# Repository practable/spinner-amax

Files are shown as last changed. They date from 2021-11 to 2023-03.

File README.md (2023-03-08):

# spinner-amax

Spinner experiment with Maxxon AMAX 32 motor, upgraded for 2022 usage by Controls and Instrumentation 3, School of Engineering, University of Edinburgh. This design has now been used for over 2,500 hours in total across 12 separate instances. We have now expanded the fleet to 48 experiments, with 12 different weights (four of each).

You can cite the contents of this repo via this paper:

D.Reid, J. Burridge, D. Lowe, T. Drysdale "Open-source remote laboratory experiments for controls engineering education," _International Journal of Mechanical Engineering Education_, February 2022, [doi:10.1177/03064190221081451](https://journals.sagepub.com/doi/full/10.1177/03064190221081451)

<figure>
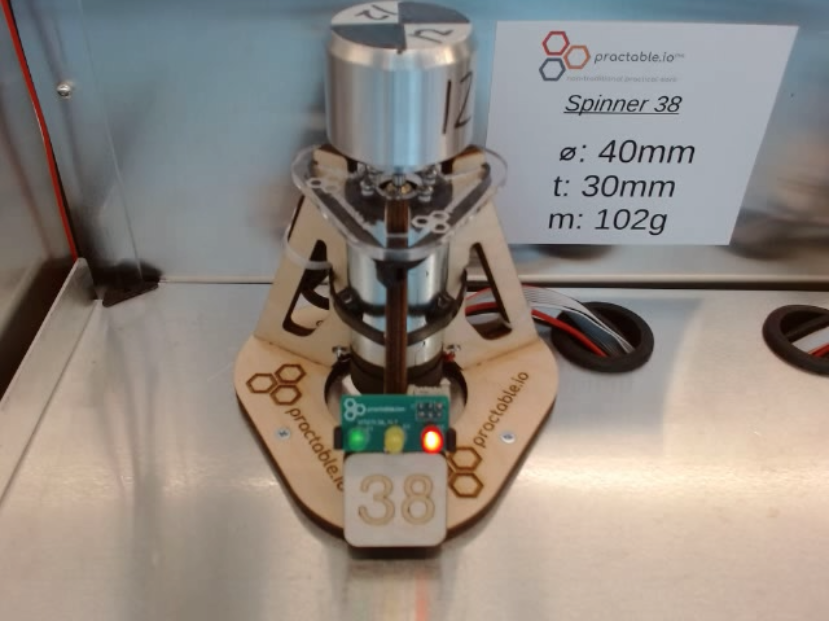
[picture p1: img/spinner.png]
Spinner hardware using Amax motor in tri-pod mount

<figcaption align = "center"><b>Fig. 1. Spinner hardware using AMAX motor</b></figcaption>
</figure>

## Contents

  - Firmware `./fw`
  - Hardware `./hw`
  - Printed Circuit Board `./hw/pcb`
  - Single Board Computer `./sbc`
  - UI `./ui`
   
## Hardware

For drawings/CAD files, please look [here](./hw/cad):

[dimensioned drawing of a weight](./hw/cad/weight-drawing.pdf)

[STEP file for the spinner experiment](./hw/cad/spinner.step)

<!--- 
<figure>
<img src="./img/spinner-cad.png"alt="3D CAD drawing of the spinner using an Amax motor in tri-pod mount" style="width:80%">
<figcaption align = "center"><b>Fig. 2. CAD drawing of the spinner hardware</b></figcaption>
</figure>
--->

### Motor

The experiment is now using an AMAX 32 motor variant (part number: 236668)

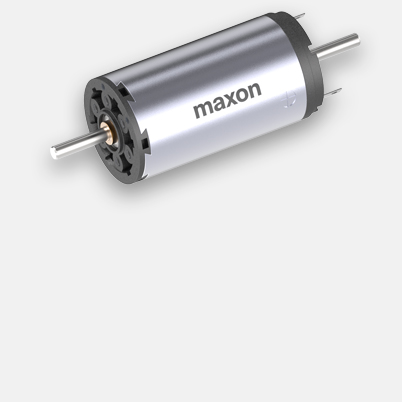
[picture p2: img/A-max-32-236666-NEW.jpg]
motor


The technical specs are [here](./hw/doc/EN-21-176.pdf/)

### Weights

The latest iteration of the weights includes attention to reducing eccentricity to reduce side load on the motor bearings.

### Previous hardware version

The first version of the hardware used a motor with siginficantly more friction, which is educationally useful although increases the challenge level for students just learning the control theory for the first time because the variability induced by the friction can obscure the presence/absence of steady state errors arising from control theory considerations. First version hardware details:  [spinner-nidec](https://github.com/practable/spinner-nidec).

## Performance

The varaibility of the step response is reduced significantly compared to the spinner using the nidec motor.
Meanwhile, here is a measured step response (average of seven runs)

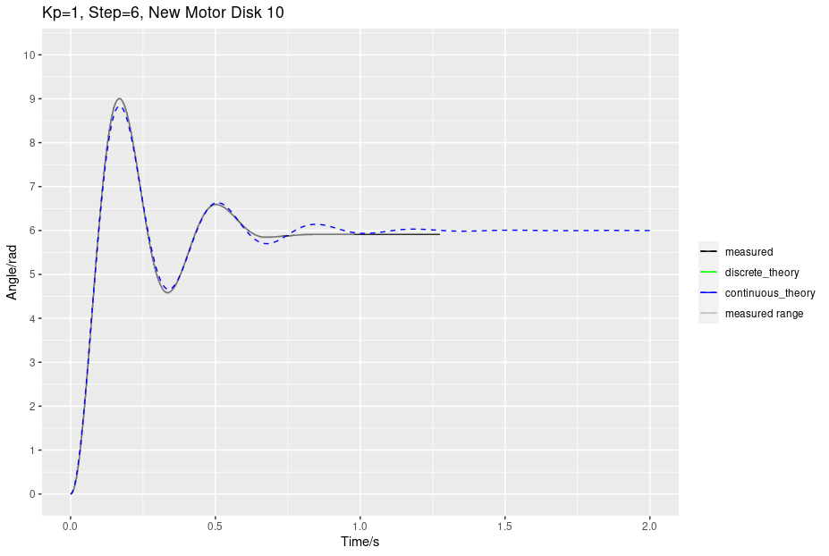
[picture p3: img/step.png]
step


## PCB

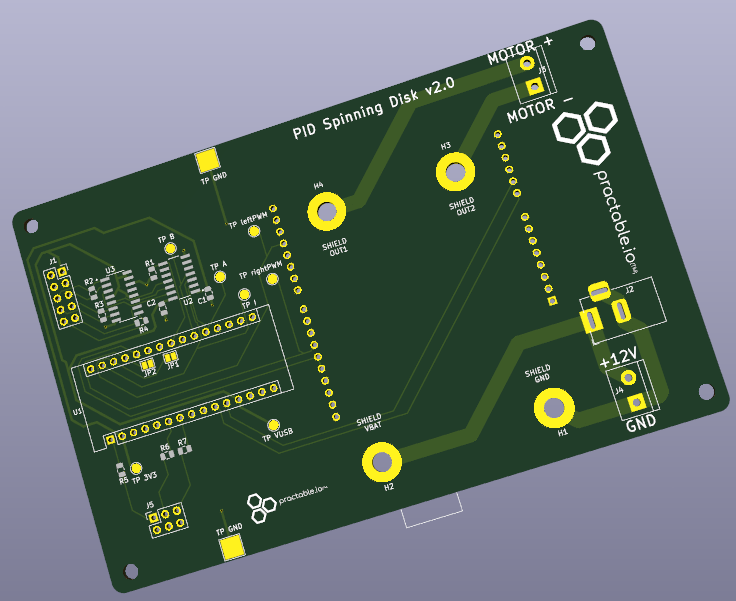
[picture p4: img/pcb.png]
pcb

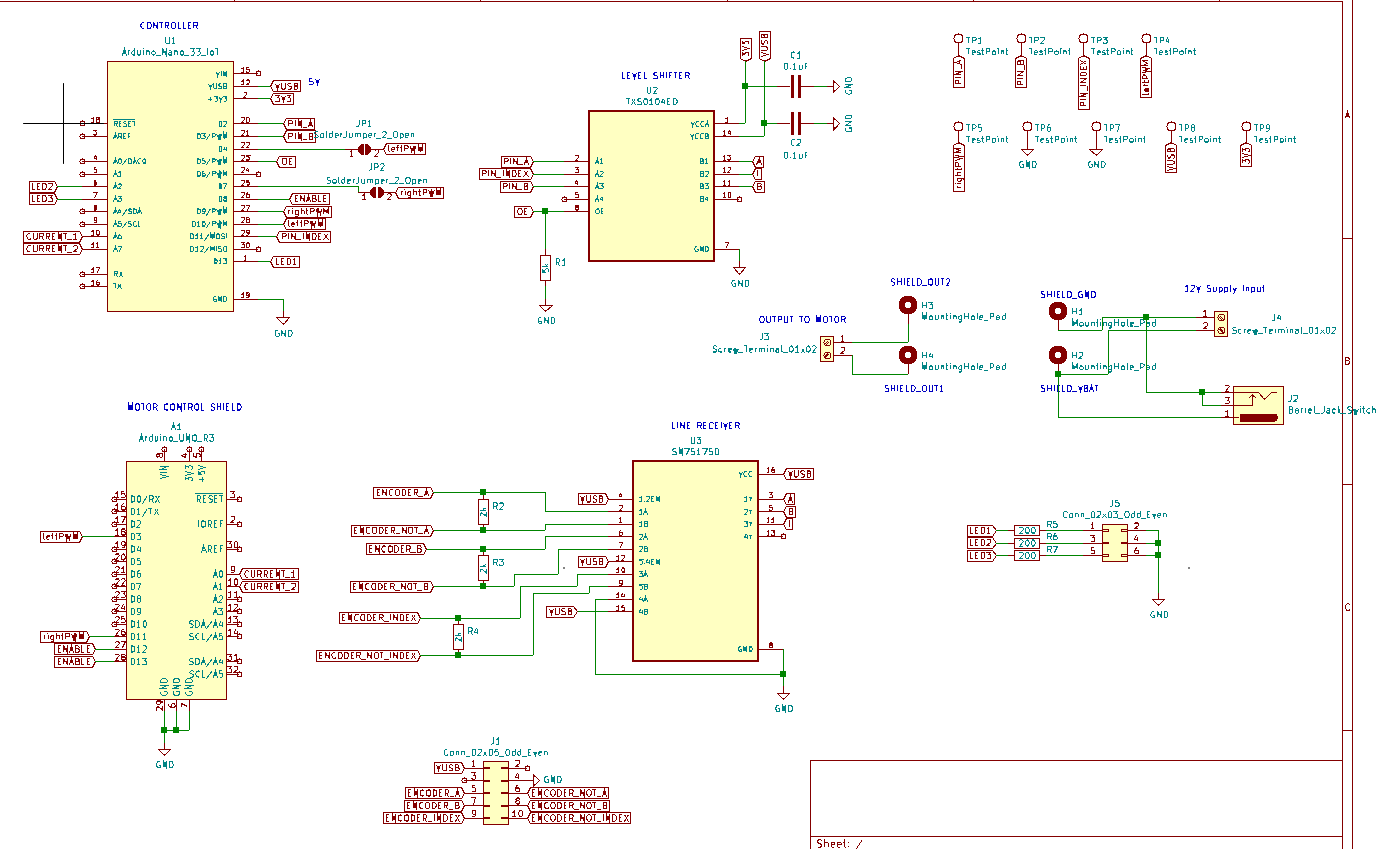
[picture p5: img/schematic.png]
schematic


## SBC

The scripts to setup your single board computer (in this case, a Raspberry Pi 4 Model B). See the [SBC README](./sbc/README.md) for instructions.

### Token refresh

Refreshing the tokens after installation is a manual process, because shell-relay currently cannot handle ansible connections.

#### Procedure

Use the configure script in `spinner-amax/sbc/scripts` to generate new tokens

```
./configure spin 30 41 https://relay-access.practable.io https://shell-access.practable.io https://shell-access2.practable.io
```

ssh into the spinners one by one (either using the shell-relay connection, or directly). If the shell tokens have expired, then a direct connection is the only option.

```
sudo su
cd /etc/practable
cat data.access #check which experiment 
rm *.token
nano data.token #copy in the token from file in ../autogenerated
nano video.token #copy in token from the file in ../autogenerated
systemctl restart session-rules
cd /usr/local/bin
mv shell shell-relay
cd /etc/systemd/system
systemctl disable shellhost #let's not use the old version any more
nano shellhost2.service #copy in file from ../autogenerated
systemctl enable shellhost2.service
systemctl start shellhost2.service
```

then check the connections to the servers

```
# in admin-tools on admin machine
./sessionrelay/getSessionStats.sh | grep spin
./shellrelay/getShellStats2.sh | grep spin
```

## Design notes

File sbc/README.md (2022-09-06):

# rpi-spinnner-2.0
How to set up a Raspberry Pi to run a spinner 2.0 experiment. 

The process is fairly simple
0. Image an SD Card with RPI OS Lite and configure it to allow ssh
0. Connect up to RPI to power, network and a Nano IoT33 
0. Log in to check you have ssh access
1. Run a configure script on your admin machine
2. Run three ansible playbooks on your admin machine (which set things up on the rpi over ssh)
3. Reboot your RPI
3. Your experiment should be working

## Abbreviations

- BYOD - Bring Your Own Device
- OS - Operating System
- SBC - single board computer (Raspberry Pi, Odroid, etc)

## Formatting

### Trimming information

`<snip>` is used to denote that line(s) have been removed for clarity

```
something useful
<snip>
other useful stuff
```

#### repo location

`$this_repo` is used to indicate the root of the git repo for clarity in the documentation, and does not actually occur in any of the scripts.

### Indicating where to enter commands?

Code snippets will sometimes clarify which machine they should be run on, if it is not obvious from the context. E.g. your local admin machine:
```
# local
$ <some commands>
```

or on the raspberry pi (via the ssh connection you've established from your local machine). 

```
# rpi
$ <some command>
```

## Prequisites

### Hardware

This is our tested configuration. 

- Raspberry Pi 4 Model B 4 GB RAM 
- SD Card 32 GB, Class 10
- USB A to micro B cable for arduino
- Arduino Nano IOT33
- USB Webcam (Logitech C920)
- USB C power cable
- RJ45 Ethernet connection (avoid WiFi because it is laggy for users)
	
For assembling the full experiment, you will also need some additional items that are outside the scope of this repo:
- Spinner PCB including Infineon motor driver board
- Spinner hardware (stand, motor, encoder, disk)
- Experimental tray and 1/6th scale shipping container

### Software

The setup is best done from a linux machine. We have no plans to support commercial operating systems.

- Linux 
   - recommend Ubuntu 20.04 LTS
- Raspberry Pi Imager
   - [github](https://github.com/raspberrypi/rpi-imager) (see link in README for latest download location)
- Practable's [relay](https://github.com/practable/relay) 
    - ensure the `sessionrelay` and `shellrelay` commands are in your path 
- Ansible 
   - Tasks developed with v2.9.17 and python 3.7.4
   - [Installation](https://docs.ansible.com/ansible/latest/installation_guide/intro_installation.html)
   
### Information

You will need either access tokens or the access secret(s) to your relay(s). Your site administrator for practable will advise. These scripts are written for the case you have the secret. If you have been provided some tokens, you just copy them into `$this_repo/autogenerated` and skip some steps where indicated.

We assume that your relay access secret is the same for all the relays in use, and available at `~/secret/practable.pat`. That way, it's not in the repo.

### Network

You need a wired staging network where unknown devices can obtain an IP address via DHCP. Your admin machine is ideally also in the same subnet as your RPI. If you are at work/university, then you will need to create your own staging network because most institutional networks prevent unknown devices from accessing the wired networks. Without a staging network, you are are stuck in a catch-22 of not knowing enough about the device to get that permission for access to the production network (typically a BYOD network for devices that staff and students might bring in).

Good staging networks: your home network (no re-configuration is needed) or a linux laptop with a wifi connection and an RJ45 dongle (share the wifi to the dongle) - I use one for initial setups and the other for ad-hoc direct connections to experiments during field-testing.

### User environment

#### Mandatory

None listed

#### Optional

If you see `ap` in the commands here, it's due to my habitual usage of a zsh alias for `ansible-playbook`. You can set up the alias by adding this line to your Zsh configuration in `~/.zshrc`:

```
alias ap="ansible-playbook"
```

I'll aim to make all code-snippets here independent of that alias.

## Setup

Overview: The process starts by loading an OS onto an SD card, modifying it to permit `ssh` access, then finishing the setup over an ssh connection. There are a mixture of steps conducted on the SBC

### SBC OS

#### Base Image

Use the Raspberry Pi Imager to image your SD Card with `Raspberry Pi OS (other) ... Raspberry Pi OS Lite (32-bit)` 

Do not bother with the full version - the desktop features are not needed but use additional power.

You'll be asked to enter your sudo password and confirm the correct SD card location - best to remove other SD cards to avoid making a mistake and choosing your camera's SD card by accident.

After verifying the card is complete, it will be mounted on your system. Do not remove it from your reader yet, and leave it mounted for the next step.

#### Modifications

You should enable `ssh` - whilst the SD Card is still mounted on your computer, look for the book partition of the SD card in your file explorer.

Open the boot partition in a terminal, and create the file `ssh`

```
touch ssh
```

Exit the terminal, unmount/eject the `boot` and `rootfs` partitions, and remove the SD card from the reader.

### RPI OS

#### Find the IP address of your RPI

Before booting your RPI, you need to figure out the IP addresses of other devices on your network. In the next step, we will be looking for the IP address of the RPI, and it is easier if you already know which devices are NOT the RPI.

First, let's figure out the IP address of the wired ethernet port on your admin machine 
```
$ ip addr 
<snip>
3: enp0s31f6: <BROADCAST,MULTICAST,UP,LOWER_UP> mtu 1500 qdisc fq_codel state UP group default qlen 1000
    link/ether xx:xx:xx:xx:xx:xx brd ff:ff:ff:ff:ff:ff
    inet 192.168.0.46/24 brd 192.168.0.255 scope global dynamic noprefixroute enp0s31f6
       valid_lft 784687sec preferred_lft 784687sec
    inet6 xxxx::xxxx:xxxx:xxxx:xxxx/64 scope link noprefixroute 
       valid_lft forever preferred_lft forever
<snip>
```
Our network card is at 192.168.0.46. The first three number groups matter here. Find all the devices on the same sub-net, using that IP address by set the last number group to `1/24` which is [shorthand](https://www.ietf.org/rfc/rfc1878.txt) for 0-254 (all possible IP in the subnet).
```
$ sudo nmap -sP 192.168.0.1/24
sudo nmap -sP 192.168.0.1/24
Starting Nmap 7.80 ( https://nmap.org ) at 2022-08-25 13:18 BST
Nmap scan report for _gateway (192.168.0.1)
Host is up (0.0016s latency).
MAC Address: xx:xx:xx:xx:xx:xx 
Nmap scan report for 192.168.0.29
Host is up (0.00059s latency).
MAC Address: xx:xx:xx:xx:xx:xx 
Nmap scan report for 192.168.0.52
Host is up (0.036s latency).
MAC Address: xx:xx:xx:xx:xx:xx 
Nmap scan report for 192.168.0.62
Host is up.
Nmap done: 256 IP addresses (3 hosts up) 
```

Put the SD card in your Raspberry Pi, connect the network cable, and power on. Wait about a minute (or repeat until a new device shows up)

```
$ sudo nmap -sP 192.168.0.1/24
sudo nmap -sP 192.168.0.1/24
Starting Nmap 7.80 ( https://nmap.org ) at 2022-08-25 13:18 BST
Nmap scan report for _gateway (192.168.0.1)
Host is up (0.0016s latency).
MAC Address: xx:xx:xx:xx:xx:xx 
Nmap scan report for 192.168.0.29
Host is up (0.00059s latency).
MAC Address: xx:xx:xx:xx:xx:xx 
Nmap scan report for 192.168.0.52
Host is up (0.036s latency).
MAC Address: xx:xx:xx:xx:xx:xx 
Nmap scan report for 192.168.0.62
Host is up.
MAC Address: yy:yy:yy:yy:yy:yy (Raspberry Pi Trading)
Nmap scan report for 192.168.0.184
Host is up (0.00027s latency).
Nmap done: 256 IP addresses (4 hosts up) 
```
Now you should see a new device that is labelled as a Raspberry Pi. If this step does not work, then the SD Card is corrupt, the network cable/power are disconnected, or the router on your network is not permitting DHCP requests from unknown devices.

In this case the IP address is 192.168.0.184.

Make a note of the MAC address of your SBC so that you can share that with your network administrators at the University - sometimes you must declare the MAC address to be able to access a wired BYOD network.

#### ssh into your RPI

The standard user and password on the image is usually `pi/raspberry`

On your machine, open a terminal
```
$ ssh pi@192.168.0.184 #change to whatever IP you found in previous step

The authenticity of host '192.168.0.184 (192.168.0.184)' can't be established.
ECDSA key fingerprint is SHA256:/0jZ9w8zL4h94rojSnSQ0Yewv5G8qK2AjCod/09pBkE.
Are you sure you want to continue connecting (yes/no/[fingerprint])? yes
Warning: Permanently added '192.168.0.184' (ECDSA) to the list of known hosts.
pi@192.168.0.184's password: <--- enter the password here (usually, raspberry)

```
Then you should see something like this:

```
Linux raspberrypi 5.10.17-v7l+ #1414 SMP Fri Apr 30 13:20:47 BST 2021 armv7l

The programs included with the Debian GNU/Linux system are free software;
the exact distribution terms for each program are described in the
individual files in /usr/share/doc/*/copyright.

Debian GNU/Linux comes with ABSOLUTELY NO WARRANTY, to the extent
permitted by applicable law.

SSH is enabled and the default password for the 'pi' user has not been changed.
This is a security risk - please login as the 'pi' user and type 'passwd' to set a new password.

Wi-Fi is currently blocked by rfkill.
Use raspi-config to set the country before use.

pi@raspberrypi:~ $ 
```

Change the password 

```
$ passwd
```

Ideally we would also set up ssh certificates but this is a future step.

You can now exit the session - we will do the next steps using ansible.

```
# rpi
$ exit
```

### SBC software and configuration

We need to generate some configuration files that are customised to your experiment. Your local admin for the practable system will advise on any naming conventions that apply at your site, as well as providing the relay key(s) which you need. 

This example is written for the case of configuring a single experiment (`spin32`) which genuinely, in this case, suffered a corrupted SD card after a successful semester of usage, and needs replacing with a fresh one).

#### Ansible hosts file

We need to let ansible know about this host.

```
sudo nano /etc/ansible/hosts
```
Add in a section like this (or modify an existing section if you have one)

```
<snip>
[rpispinnerv2]
spin32 ansible_host=192.168.0.184 practable_label=spin32

[rpispinnerv2:vars]
ansible_connection=ssh
ansible_user=pi
ansible_password=***REMOVED***
<snip>
```

#### Practable connections

We need to configure routing and tokens for the video, data, shell, and shell2 connections. There are scripts provided to help you. They put files into `$this_repo./autogenerated`

Create the configuration files we need, assuming we are using the standard practable relay URLs.

```
#local
cd scripts
.configure spin 32 32 https://relay-access.practable.io https://shell-access.practable.io https://shell-access2.practable.io
```

##### Session

Now we can run our ansible playbooks - these each take some time, so get the kettle ready. It's nearly as fast doing multiple machines, because the playbooks are run in parallel. There is no need to do each RPI separately one after another.

```
#local
cd playbooks
ansible-playbook install-session
ansible-playbook install-shell
ansible-playbook install-firmware
```

If those commands go smoothly, then you are done with the install. If not, check out the troubleshooting guide below.

## Checking the installation

Go to the booking page link the adminstrator gave you, and you should be able to access/control the experiment. 

## Troubleshooting

If things are not working right, then you might be able to fix them by troubleshooting. 

### No DHCP

This is usually caused by 
- SD Card corrupt
- network administrator is unaware of the MAC address of the wired network port on the SBC

### No SSH connection

Since `sshd` is not enabled by default, you must enable it (see instructions) before incoming connections on port 22 will be accepted.

### Remote host identification has changed

If you work with a lot of experiments, sooner or later an old IP address on your staging network will be re-assigned to a new experiment you are setting up, and then you will see something like this:

```
@@@@@@@@@@@@@@@@@@@@@@@@@@@@@@@@@@@@@@@@@@@@@@@@@@@@@@@@@@@
@    WARNING: REMOTE HOST IDENTIFICATION HAS CHANGED!     @
@@@@@@@@@@@@@@@@@@@@@@@@@@@@@@@@@@@@@@@@@@@@@@@@@@@@@@@@@@@
IT IS POSSIBLE THAT SOMEONE IS DOING SOMETHING NASTY!
Someone could be eavesdropping on you right now (man-in-the-middle attack)!
It is also possible that a host key has just been changed.
The fingerprint for the ECDSA key sent by the remote host is
SHA256:/0jZ9w8zL4h94rojSnSQ0Yewv5G8qK2AjCod/09pBkE.
Please contact your system administrator.
Add correct host key in /home/tim/.ssh/known_hosts to get rid of this message.
Offending ECDSA key in /home/tim/.ssh/known_hosts:178
  remove with:
  ssh-keygen -f "/home/tim/.ssh/known_hosts" -R "192.168.0.184"
ECDSA host key for 192.168.0.184 has changed and you have requested strict checking.
Host key verification failed.
```

Simply run the suggested command, and then carry on where you left off with trying to connect over `ssh`. The command is unique each time it happens (you're overwriting an entry in the known-hosts file so it must correspond to the host causing the problem _this_ time). E.g.

```
$ssh-keygen -f "/home/tim/.ssh/known_hosts" -R "192.168.0.184"

# Host 192.168.0.184 found: line 178
/home/tim/.ssh/known_hosts updated.
Original contents retained as /home/tim/.ssh/known_hosts.old
```

### Check the OS
If you're not sure if you have the right OS for the ansible scripts, you can check. For this experiment, you should see something like this

```
$ uname -a
Linux raspberrypi 5.10.17-v7l+ #1414 SMP Fri Apr 30 13:20:47 BST 2021 armv7l GNU/Linux
```

### Ansible cannot reach rpi

If you are having trouble connecting via ansible, following the guidance on verbose logging [here](https://docs.ansible.com/ansible/latest/network/user_guide/network_debug_troubleshooting.html)

You might find you've got the format of the /etc/ansible/hosts incorrect (e.g. didn't name the vars section correctly, got the password wrong etc).

### ttyACM0 Device not found 

If you get this error, reboot the raspberry pi and try again. If the error persists, check which device name it has been assigned (`/dev/ttyACM0` is expected for Nano 33 IOT)
```
#rpi
lsusb
dmesg | tail
```

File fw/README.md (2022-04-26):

# spinner-amax-firmware
Arduino Nano 33 IOT Firmware for the [amax-spinner](https://github.com/practable/spinner-amax) hardware

## About

This firmware is intended to work with the [amax-spinner](https://github.com/practable/spinner-amax) hardware as shown in Fig. 1.

<figure>
Spinner hardware using Amax motor in tri-pod mount
<figcaption align = "center"><b>Fig. 2. Spinner hardware using AMAX motor</b></figcaption>
</figure>

The firmware is configured to use a printed circuit board designed according to the schematic in Fig. 2.
<figure>
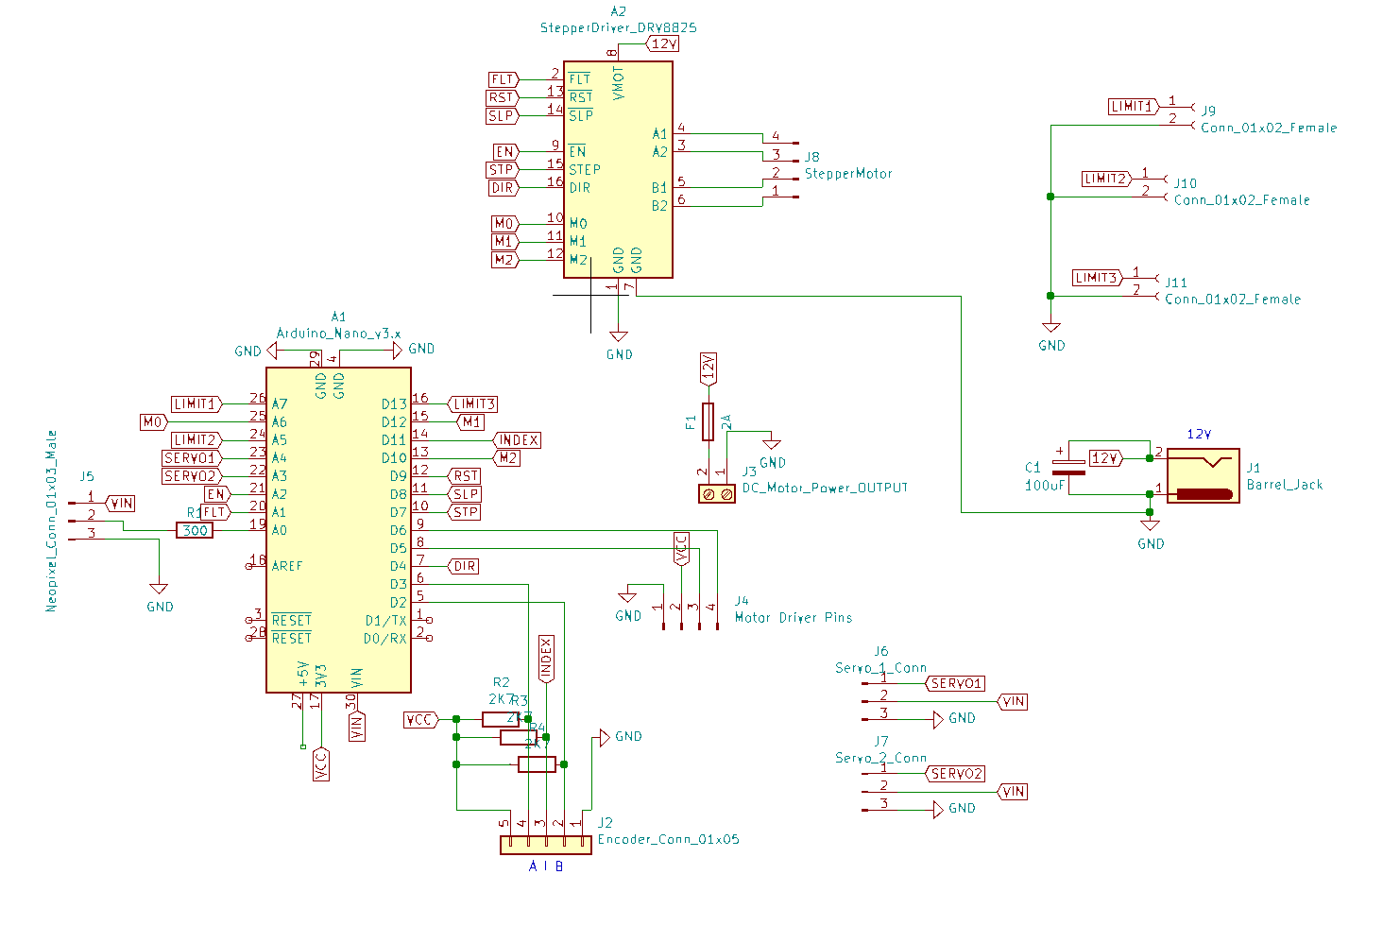
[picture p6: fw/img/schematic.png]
Spinner circuit schematic

<figcaption align = "center"><b>Fig. 2. Spinner circuit schematic</b></figcaption>
</figure>

## History

This firmware was developed in [dpreid/pidcontroller](https://github.com/dpreid/pidcontroller), and covered several different experiments based around a brushed DC motor. One of the experiments (this one) has been significantly upgraded (new motor, encoder) so the firmware has been split off into this repo to avoid confusion. The starting point for this repo is the code that was used to deliver over 2,500 hours of experiments in the early part of 2022.

## Contents

The repo contains several directories, with the code in `SpinningDiskController.`

### ./SpinningDiskController

This is the arduino firmware itself - note that the Arduino convention is to use camel case with an initial capital letter, and that the folder name should match the sketch name.

### ./libraries

These are the libraries required by the firmware 

### ./test

This directory contains tests - see [./test/README.md](./test/README.md) for details.

### ./scripts

This directory contains scripts to compile and upload, and an example ansible task for a raspberry pi running pios.

## Usage

The 'upload.sh' script will compile and upload the firmware, assuming you have a working command-line development environment for the Arduino Nano 33 IOT.

### Installing firmware on raspberry pi via cli

If you have installed the `arduino-cli` but not yet compiled for the Nano IOT 33, then add support for this hardware by 

```
arduino-cli core update-index
arduino-cli core install arduino:samd
```

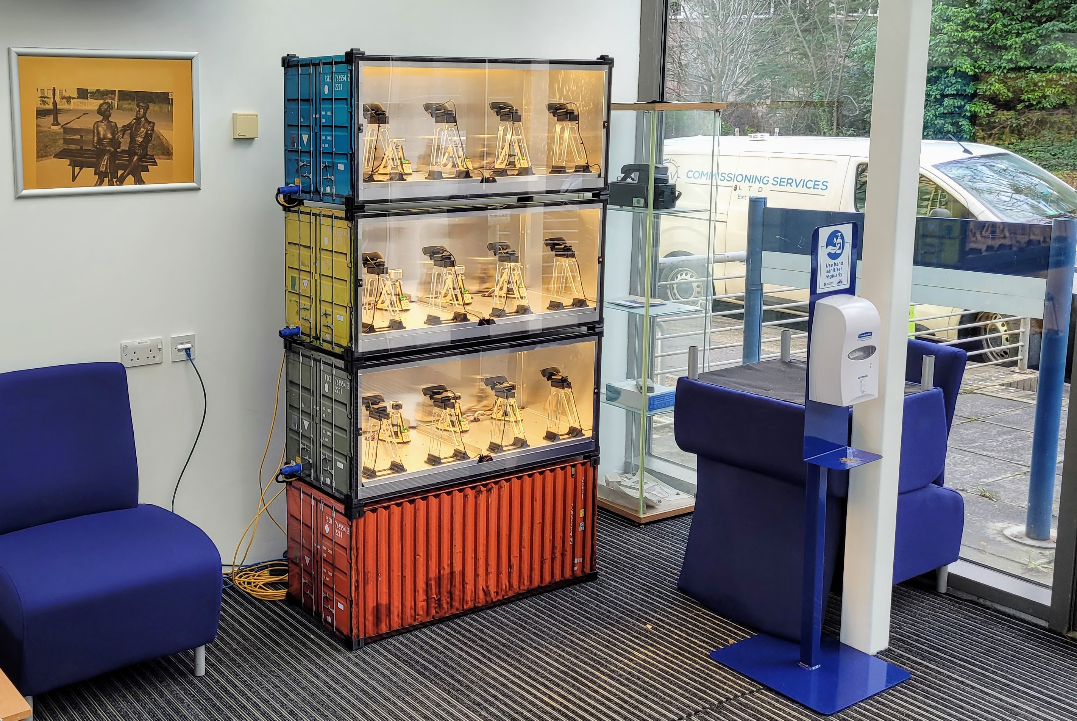
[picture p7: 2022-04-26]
fw/img/AGB_Spinners.jpg

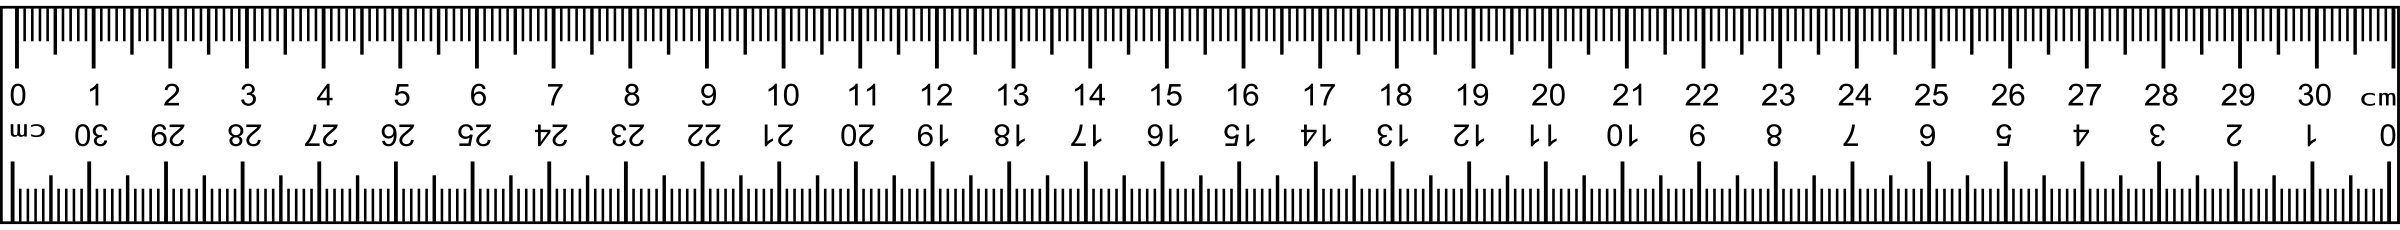
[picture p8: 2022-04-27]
ui/default/src/assets/ruler.png

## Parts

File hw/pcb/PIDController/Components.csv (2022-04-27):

Comment | Designator | Footprint | JLCPCB Part #（optional）
2k | R4,R2,R3 | R_0805_2012Metric | C17604
 | REF**,REF**,REF**,REF** | MountingHole_3.2mm_M3
 | A1 | Arduino_UNO_R3
SN75175D | U3 | SOIC127P600X175-16N
C474952 | J3,J4,J5,J6 | TerminalBlock_bornier-2_P5.08mm | C474952
 | U1 | MODULE_ABX00027
TXS0104ED | U2 | SOIC127P600X175-14N
C5665 | J1 | PinSocket_2x05_P2.54mm_Vertical | C5665
C11214 | J7 | PinSocket_2x03_P2.54mm_Vertical | C11214
 | JP1,JP2 | SolderJumper-2_P1.3mm_Open_Pad1.0x1.5mm
 | TP A,TP B,TP I,TP leftPWM,TP rightPWM,TP VUSB,TP 3V3 | TestPoint_Pad_D2.0mm
 | TP GND,TP GND | TestPoint_Pad_4.0x4.0mm
0.1uF | C1,C2 | C_0805_2012Metric | C49678
5k | R1 | R_0805_2012Metric | C78980
200 | R5,R6,R7 | R_0805_2012Metric | C17540

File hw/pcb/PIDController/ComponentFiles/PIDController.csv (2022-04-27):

Comment | Designator | Footprint | JLCPCB Part #（optional）
 | G*** | practableLogo36x15
 | G*** | practable-logo-larger
 | REF**,REF**,REF**,REF** | MountingHole_3.2mm_M3
2k | R4,R2,R3 | R_0805_2012Metric | C17604
 | A1 | Arduino_UNO_R3
SN75175D | U3 | SOIC127P600X175-16N
C474952 | J3,J4 | TerminalBlock_bornier-2_P5.08mm | C474952
TXS0104ED | U2 | SOIC127P600X175-14N
 | J1 | PinSocket_2x05_P2.54mm_Vertical
 | JP1,JP2 | SolderJumper-2_P1.3mm_Open_Pad1.0x1.5mm
 | TP A,TP B,TP I,TP leftPWM,TP rightPWM,TP VUSB,TP 3V3 | TestPoint_Pad_D2.0mm
 | TP GND,TP GND | TestPoint_Pad_4.0x4.0mm
0.1uF | C1,C2 | C_0805_2012Metric | C49678
5k | R1 | R_0805_2012Metric | C78980
200 | R5,R6,R7 | R_0805_2012Metric | C17540
 | U1 | Arduino_Nano
 | H1,H2,H3,H4 | MountingHole_4mm_Pad
 | J5 | PinSocket_2x03_P2.54mm_Vertical
 | J2 | BarrelJack_Horizontal_DC10B

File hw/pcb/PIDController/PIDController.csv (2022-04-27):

Id | Designator | Package | Quantity | Designation | Supplier and ref
1 | G*** | practableLogo36x15 | 1 | LOGO
2 | G*** | practable-logo-larger | 1 | LOGO
3 | REF**,REF**,REF**,REF** | MountingHole_3.2mm_M3 | 4 | MountingHole_3.2mm_M3
4 | R4,R2,R3 | R_0805_2012Metric | 3 | 2k
5 | A1 | Arduino_UNO_R3 | 1 | Arduino_UNO_R3
6 | U3 | SOIC127P600X175-16N | 1 | SN75175D
7 | J3,J4 | TerminalBlock_bornier-2_P5.08mm | 2 | Screw_Terminal_01x02
8 | U2 | SOIC127P600X175-14N | 1 | TXS0104ED
9 | J1 | PinSocket_2x05_P2.54mm_Vertical | 1 | Conn_02x05_Odd_Even
10 | JP1,JP2 | SolderJumper-2_P1.3mm_Open_Pad1.0x1.5mm | 2 | SolderJumper_2_Open
11 | TP A,TP B,TP I,TP leftPWM,TP rightPWM,TP VUSB,TP 3V3 | TestPoint_Pad_D2.0mm | 7 | TestPoint
12 | TP GND,TP GND | TestPoint_Pad_4.0x4.0mm | 2 | TestPoint
13 | C1,C2 | C_0805_2012Metric | 2 | 0.1uF
14 | R1 | R_0805_2012Metric | 1 | 5k
15 | R5,R6,R7 | R_0805_2012Metric | 3 | 200
16 | U1 | Arduino_Nano | 1 | Arduino_Nano_33_IoT
17 | H1,H2,H3,H4 | MountingHole_4mm_Pad | 4 | MountingHole_Pad
18 | J5 | PinSocket_2x03_P2.54mm_Vertical | 1 | Conn_02x03_Odd_Even
19 | J2 | BarrelJack_Horizontal_DC10B | 1 | Barrel_Jack_Switch

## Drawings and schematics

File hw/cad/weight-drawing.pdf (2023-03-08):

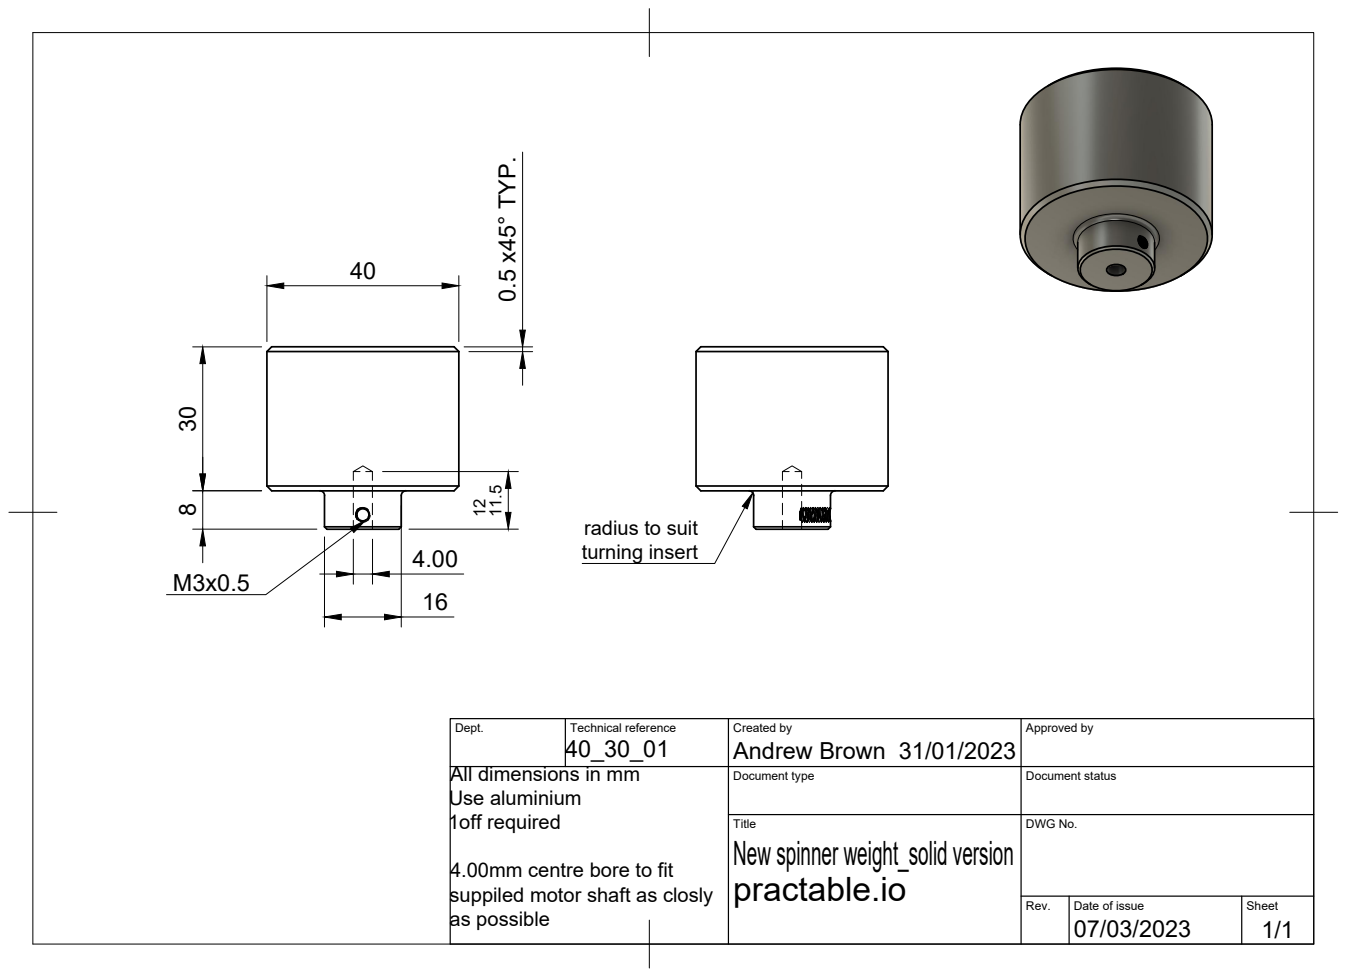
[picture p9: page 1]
as possible 30; 8 0.5 x45° TYP.

radius to suit
turning insert

Dept. | Technical reference 40_30_01 | Created by Andrew Brown 31/01/2023 | Approved by

All dimensions in mm Use aluminium 1off required 4.00mm centre bore to fit suppiled motor shaft as closly | | Document type | Document status

Title New spinner weight_solid version practable.io | DWG No.

Rev. | Date of issue 07/03/2023 | Sheet 1/1

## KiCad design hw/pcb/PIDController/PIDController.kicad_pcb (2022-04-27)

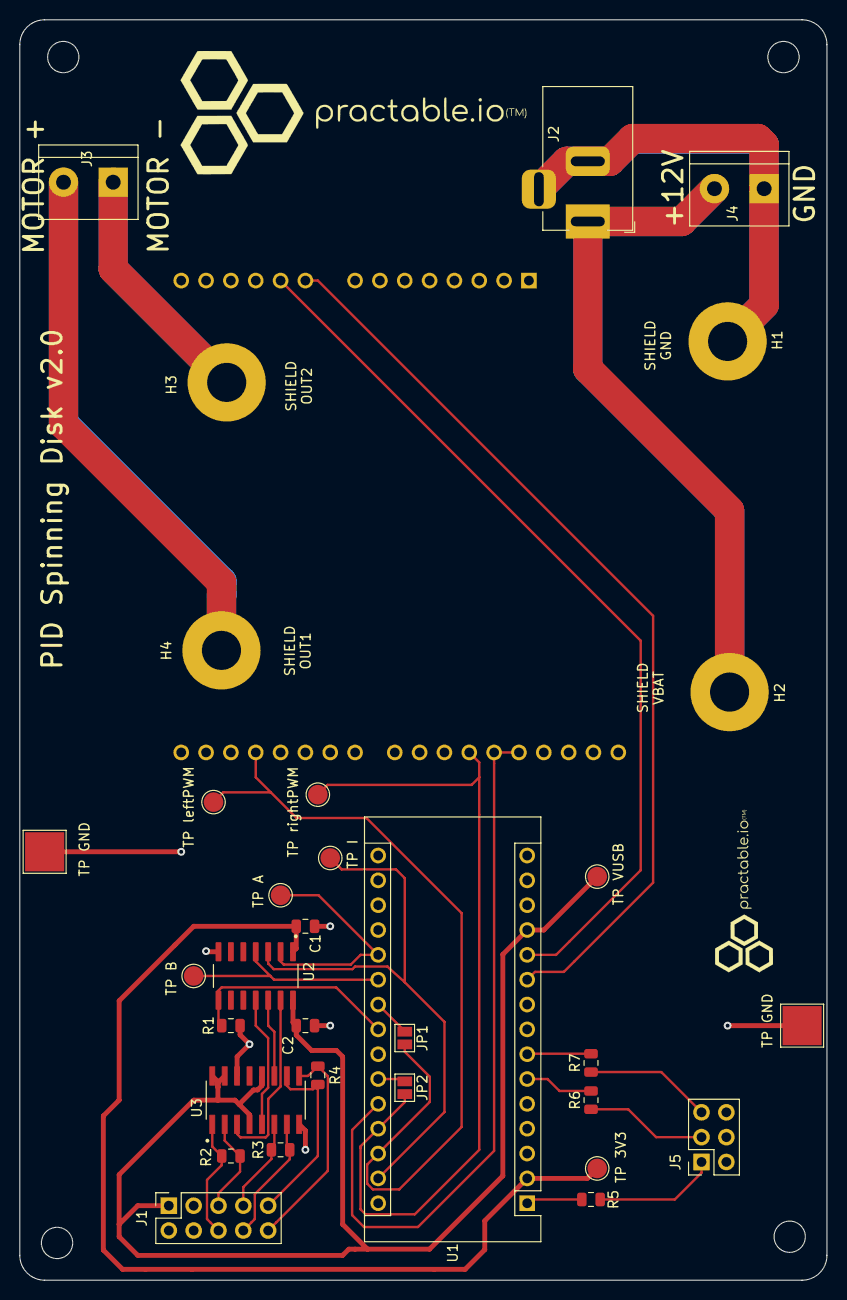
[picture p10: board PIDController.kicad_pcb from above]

Board: 2 copper layers, 82.6 x 128.9 mm, 33 parts (1 on the bottom side), 34 nets.

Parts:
A1: Arduino_UNO_R3
C1, C2: 0.1uF; C_0805_2012Metric
H1, H2, H3, H4: MountingHole_Pad; MountingHole_4mm_Pad
J1: Conn_02x05_Odd_Even; PinSocket_2x05_P2.54mm_Vertical
J2: Barrel_Jack_Switch; BarrelJack_Horizontal_DC10B
J3, J4: Screw_Terminal_01x02; TerminalBlock_bornier-2_P5.08mm
J5: Conn_02x03_Odd_Even; PinSocket_2x03_P2.54mm_Vertical
JP1, JP2: SolderJumper_2_Open; SolderJumper-2_P1.3mm_Open_Pad1.0x1.5mm
R1: 5k; R_0805_2012Metric
R2, R3, R4: 2k; R_0805_2012Metric
R5, R6, R7: 200; R_0805_2012Metric
TP 3V3: TestPoint; TestPoint_Pad_D2.0mm
TP A: TestPoint; TestPoint_Pad_D2.0mm
TP B: TestPoint; TestPoint_Pad_D2.0mm
TP GND: TestPoint; TestPoint_Pad_4.0x4.0mm
TP GND#2: TestPoint; TestPoint_Pad_4.0x4.0mm
TP I: TestPoint; TestPoint_Pad_D2.0mm
TP VUSB: TestPoint; TestPoint_Pad_D2.0mm
TP leftPWM: TestPoint; TestPoint_Pad_D2.0mm
TP rightPWM: TestPoint; TestPoint_Pad_D2.0mm
U1: Arduino_Nano_33_IoT; Arduino_Nano
U2: TXS0104ED; SOIC127P600X175-14N
U3: SN75175D; SOIC127P600X175-16N

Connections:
3V3: C1.2, TP 3V3.1, U1.2, U2.1
A: U2.13, U3.3
B: U2.11, U3.5
CURRENT_1: A1.9, U1.10
CURRENT_2: A1.10, U1.11
ENABLE: A1.27, A1.28, U1.26
ENCODER_A: J1.5, R2.1, U3.2
ENCODER_B: J1.7, R3.1, U3.6
ENCODER_INDEX: J1.9, R4.1, U3.10
ENCODER_NOT_A: J1.6, R2.2, U3.1
ENCODER_NOT_B: J1.8, R3.2, U3.7
ENCODER_NOT_INDEX: J1.10, R4.2, U3.9
GND: A1.6, A1.7, A1.29, C1.1, C2.1, J1.4, J5.2, J5.4, J5.6, R1.2, TP GND.1, TP GND#2.1, U1.14, U1.19, U2.7, U3.8, U3.14
I: U2.12, U3.11
LED1: R5.2, U1.1
LED2: R6.2, U1.6
LED3: R7.2, U1.7
unnamed: H1.1, J2.2, J2.3, J4.1
unnamed: H2.1, J2.1, J4.2
unnamed: H3.1, J3.1
unnamed: H4.1, J3.2
unnamed: J5.1, R5.1
unnamed: J5.3, R6.1
unnamed: J5.5, R7.1
unnamed: JP1.1, U1.22
unnamed: JP2.1, U1.25
unnamed: U1.13, U1.18
OE: R1.1, U1.23, U2.8
PIN_A: TP A.1, U1.20, U2.2
PIN_B: TP B.1, U1.21, U2.4
PIN_INDEX: TP I.1, U1.29, U2.3
VUSB: C2.2, J1.1, TP VUSB.1, U1.12, U2.14, U3.4, U3.12, U3.15, U3.16
leftPWM: A1.18, JP1.2, TP leftPWM.1, U1.28
rightPWM: A1.26, JP2.2, TP rightPWM.1, U1.27

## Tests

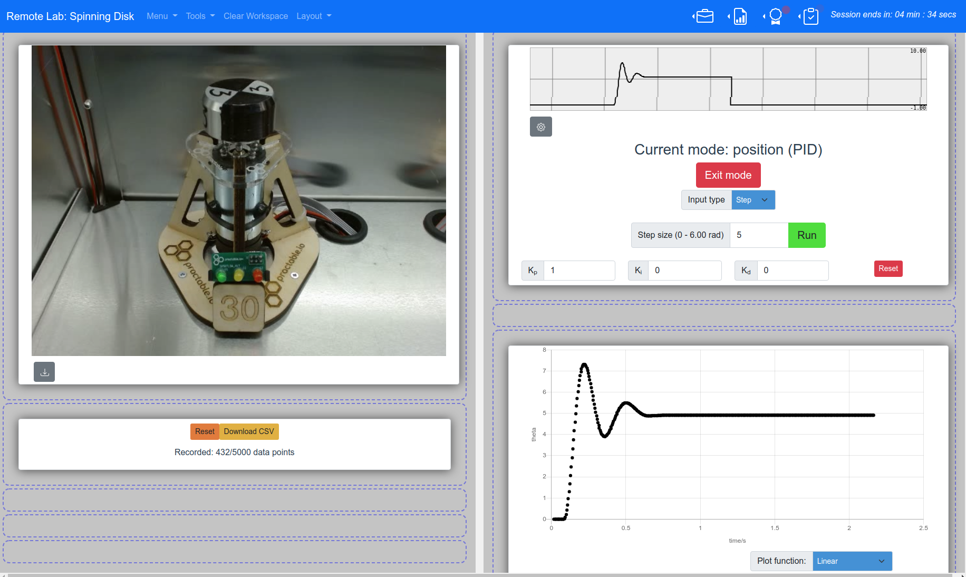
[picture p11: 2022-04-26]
fw/test/img/148185437-7db315d8-224d-4d57-81fa-598ac8901bfc.png

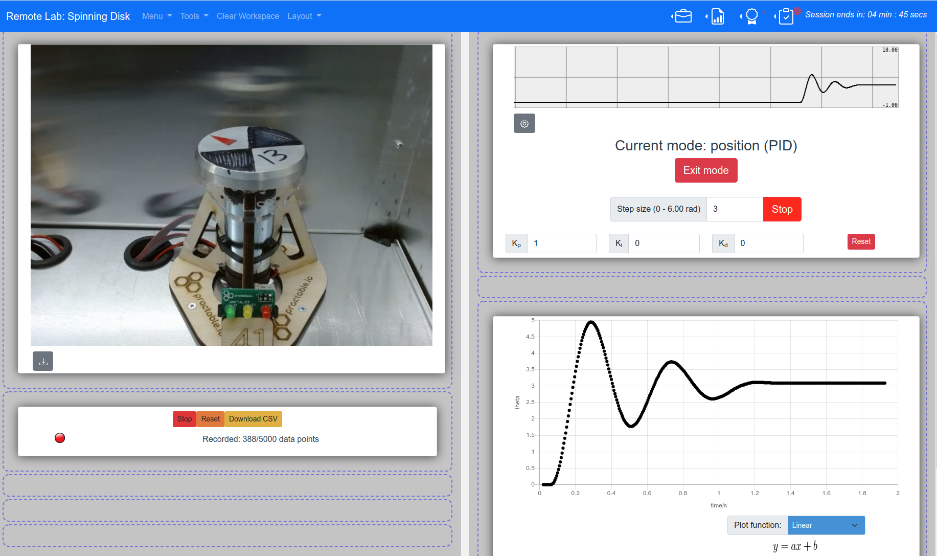
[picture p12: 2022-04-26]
fw/test/img/148185519-088c40de-2e64-4c90-8afa-47b3f1235d8f.png

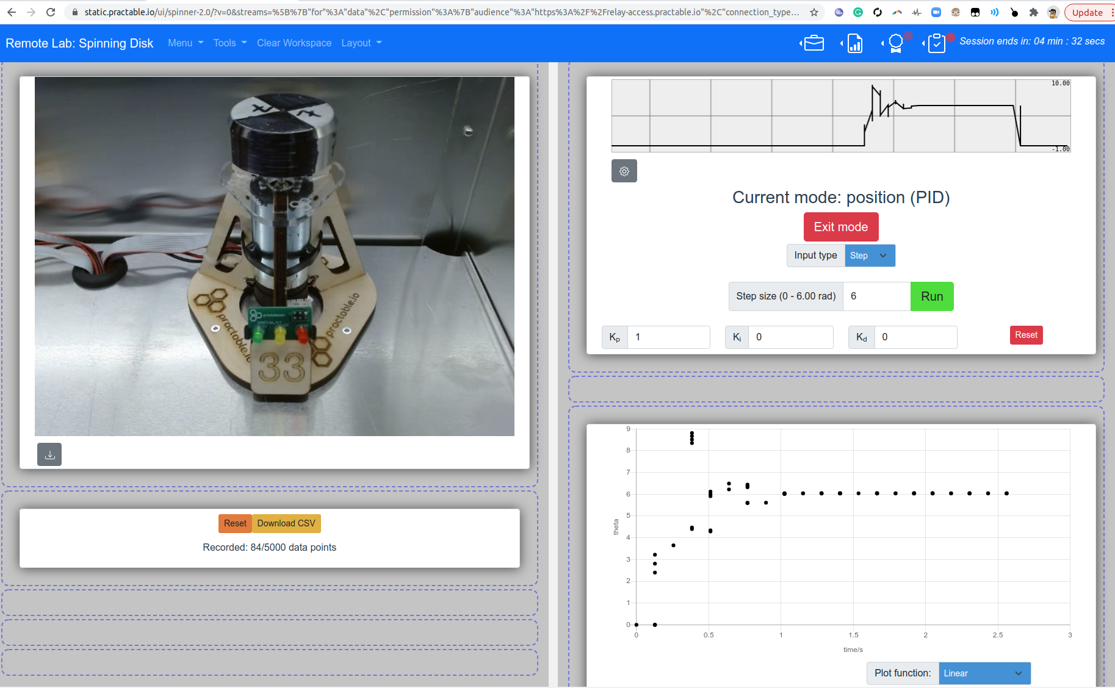
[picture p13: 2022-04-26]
fw/test/img/148067785-3ddec737-a71b-4736-8f02-44dddf6f8416.png

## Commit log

2021-11-16 Add motor info to README.md
2022-04-27 pcb and ui files added
    [Components.csv, PIDController-B_Cu.gbr, PIDController-B_Mask.gbr, PIDController-B_Paste.gbr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]
2022-08-31 limited voltage to 6V
2023-03-02 sbc (fix): pin relay v0.2.3
2024-06-20 Logging updated so that other means of sending a voltage step also register graph edges
2024-07-08 OptionsTool and PopupHelp updated to use nextTick to attach and remove modal from body to ensure correct display
